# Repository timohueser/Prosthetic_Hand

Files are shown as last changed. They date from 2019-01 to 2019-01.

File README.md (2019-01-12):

# Prosthetic_Hand_V1
## Overview
The aim of this project is to design a 3D printable hand prosthesis. The hand uses 6 cheap geared DC motors that are readily available from Ebay and other places for it's 6 degrees of freedom. Motor control is achieved through a custom made Motor driver PCB that also handles force measurements for each finger. All the 3D models in STEP and STL format are available in this repository, as well as the KiCad design files and schematic of the PCB. The hand is fully self contained and only requires an external power supply and a SPI control signal to be operated. A new version of the prosthetic hand based on this design can be found here: https://github.com/timohueser/Prosthetic_Hand_V2.
<p align="center">
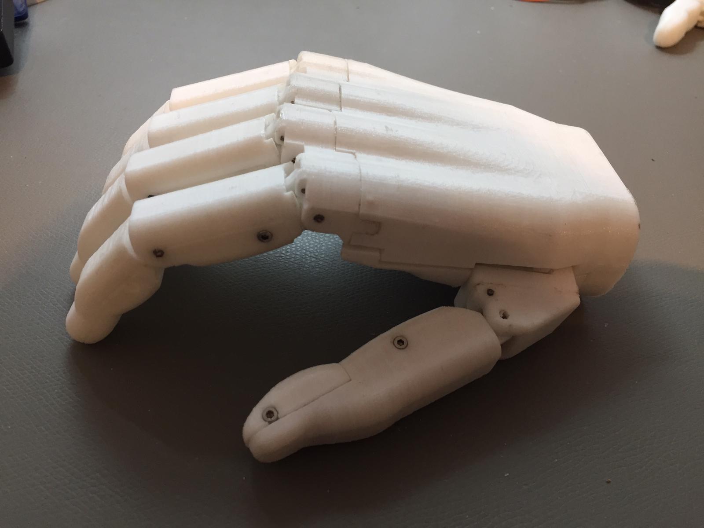
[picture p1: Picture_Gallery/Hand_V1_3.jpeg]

</p>

## Technical Details
### Fingers
The fingers are fully 3D printable and have 2 joints that move proportional to each other. It was decided to use rigid parts to drive the fingers instead of a string based system. This increases reliability and overall robustness but gives up some of the compliance that a string based system allows. The finger gets driven by a geared DC motor with a lead screw attached to its ouput shaft. A lead screw mechanism has the advantage of not being backdrivable, so the motor does not need to supply the holding torque for the fingers and only needs to be active during movement. With the motor gear ratio choosen the hand achieves reasonable movement speeds while still being able to apply ample force for tasks like picking up everyday objects. Unfortunately the way the lead screw mechanism is implemented in this version of the hand is not very durable, this is mainly due to the low quality of the lead screw and nut and the assymetric way the force gets applied to the lead screw with the current design. Version 2 of the prostehic hand mostly solves this reliability problem. Version 2 also replaces the cheap geared motors used in this version with high quality Maxon Dc motors that can produce significantly more power because of their higher efficiency. Also overall reliability of motor windings and the gearbox are obvious drawbacks of using the cheap motors compared to high quality ones. 
<p align="center">
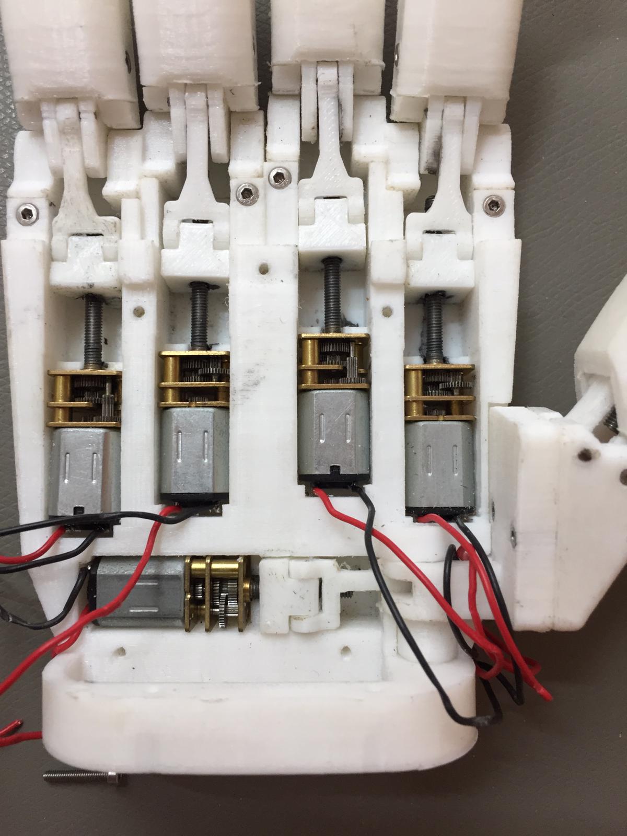
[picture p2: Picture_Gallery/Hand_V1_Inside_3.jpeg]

</p>

### Thumb
Similar to the other fingers the thumb uses a lead screw machanism to be positioned. In contrast to the other fingers the thumb has two degrees of freedom controlled by two seperate motors. One motor is placed inside the thumb itself and is responsible for flexion and extension of the thumb while the other sits inside the palm of the hand and controls abduction and adduction. This allows a variety of disserent gripping patterns, that the hand can switch bewtween quickly and without needing to be manually adjusted with the other hand. Having one of the motors inside the thumb is necessary to fit the realtively big motors choosen for this project inside the hand, but leads to a less than optimal weight distribution.
Furthermore the exact geometry, like for example the axis of rotation for abduction, still requires a lot of finetuning since the current geometry causes very unnatural positioning of the thumb for certain gripping patterns. Adding compliance to the abduction/adduction joint is a aim for version two, that is expected to greatly improve the capability of the hand to addapt do different objects.

### Motor Driver PCB
The motor driver PCB is based on the L293D Quad Half-H Driver to power the 6 DC motors. It needs to be supplied by a 9-12V motor power supply and a 3-5V supply for the logic and current sense circuitry. The motor supply should be able to handle at least 2 Amps of peak current draw. The motor driver ICs are controlled by a simple 74HC595 shift register, this enables very simple control over the hand over a standard SPI protocoll. Unfortunately there is no encoder readout for the motors for reasons of space constraint. This limits the precision the fingers can be positioned at significantly. 
In addition to motor drive capabilities the circuit also has 6 current sensors, consisting of a current sense resistor and a differential amplifier for each motor to monitor the strain on the motors. This can either be used as crude force feedback to the user of the hand or to limit the torque the hand can apply and stop motors from stalling as soon as the grip is closed. It is also useful as a homing feature since as mentioned previously there is no direct position readout for the fingers. 
Despite adding this position readout using motor drivers with better efficiency is is one of the major improvements that need to be made for the motor driver PCB used in version 2 of the prosthetic hand. The L293D drivers are very inneficient compared to more modern motor driver ICs and produce a lot of excess heat that builds up quickly in the tight and isolated environment the PCB is installed in. In addition many modern motor driver ICs have features like thermal cutoffs and motor current monitoring already built in, allowing for a much more compact PCB design. 
<p align="center">
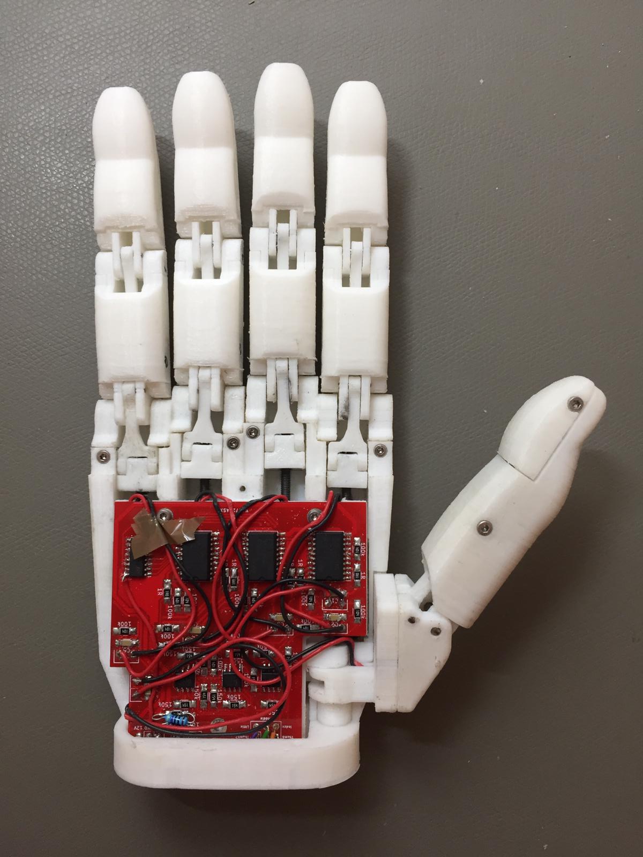
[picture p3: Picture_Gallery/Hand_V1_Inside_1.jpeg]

</p>

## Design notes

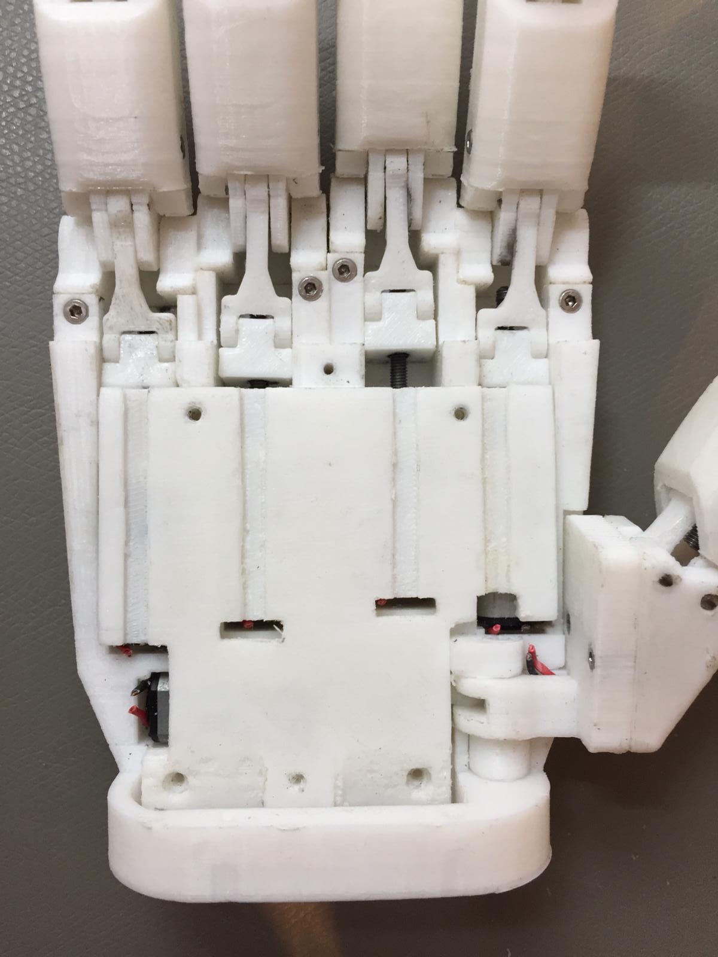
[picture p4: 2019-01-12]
Picture_Gallery/Hand_V1_Inside_2.jpeg

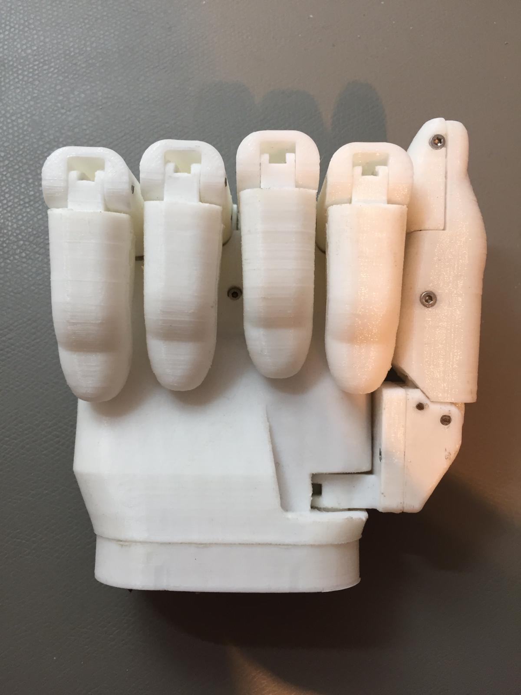
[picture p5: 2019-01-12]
Picture_Gallery/Hand_V1_2.jpeg

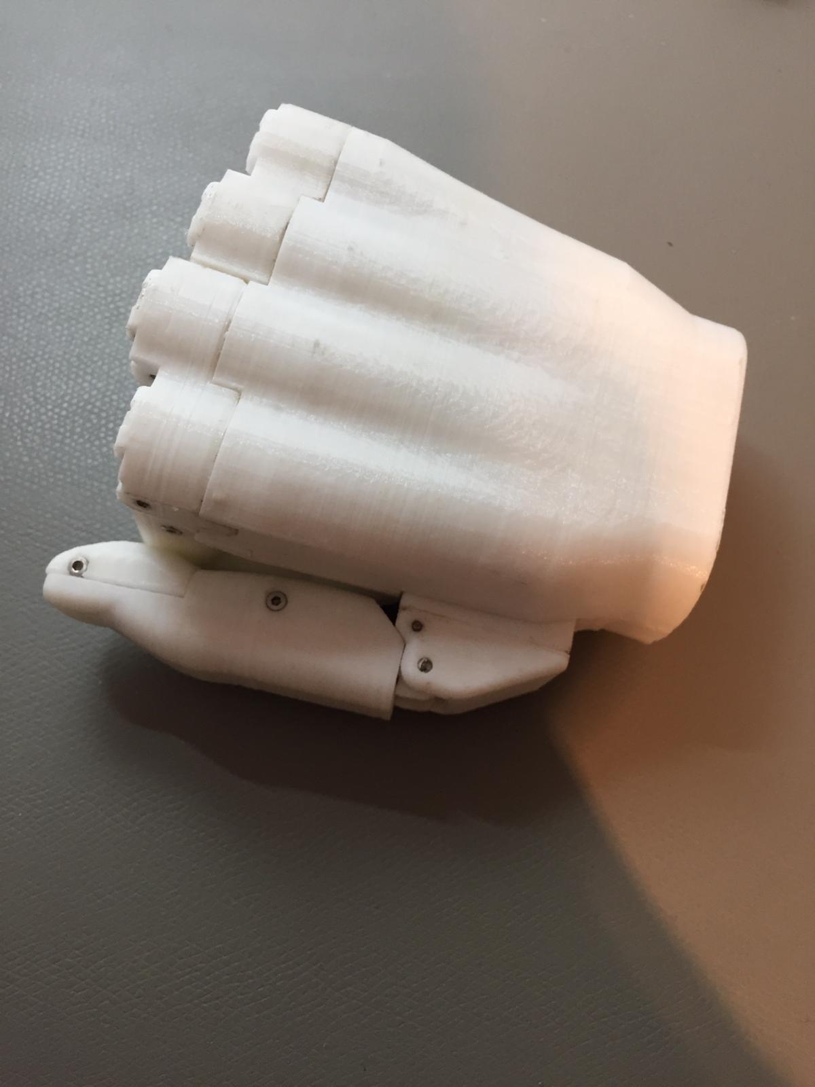
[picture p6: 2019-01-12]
Picture_Gallery/Hand_V1_4.jpeg

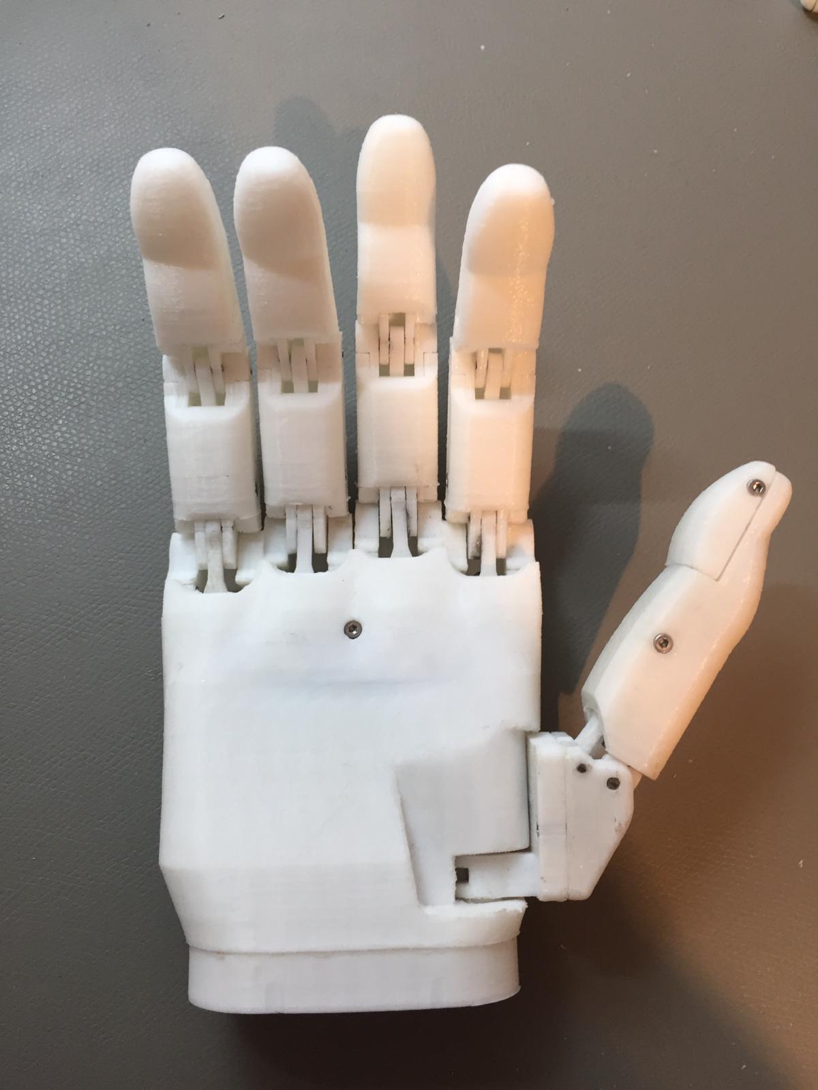
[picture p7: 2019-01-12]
Picture_Gallery/Hand_V1_1.jpeg

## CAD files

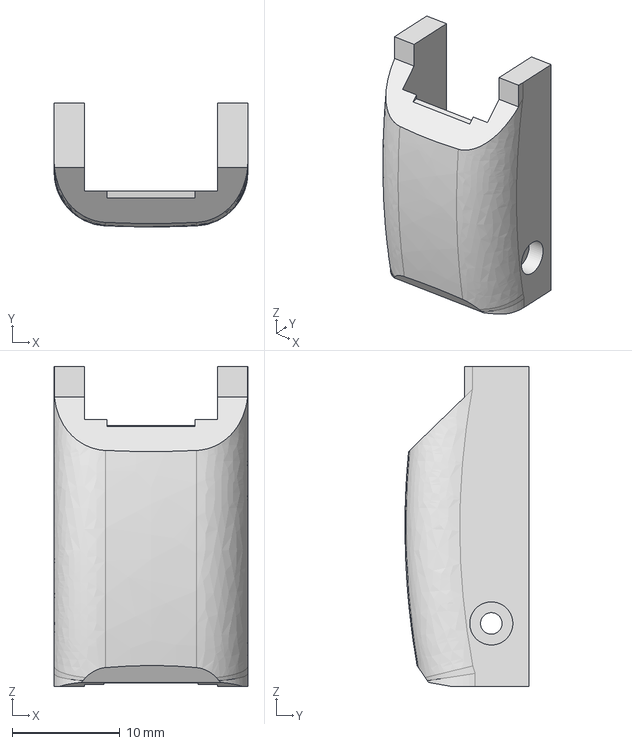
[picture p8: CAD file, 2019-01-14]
3D_Files/Finger/Lower_Part/Front.step
18.0 x 11.5 x 29.7 mm

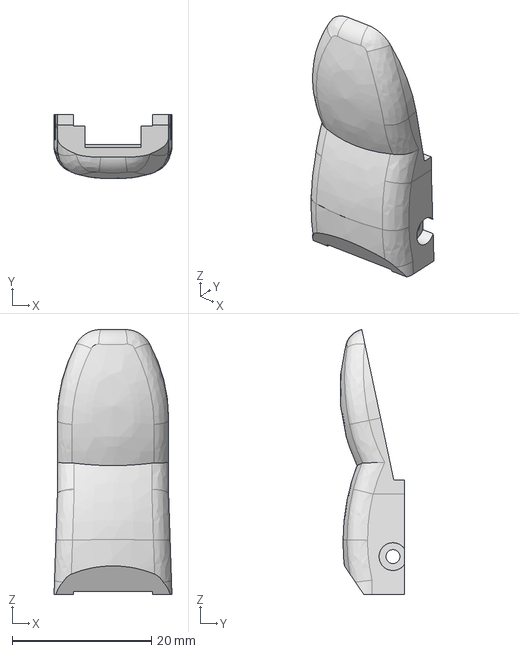
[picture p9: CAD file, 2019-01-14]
3D_Files/Finger/Upper_Part/Front.step
17.0 x 9.19 x 38.1 mm

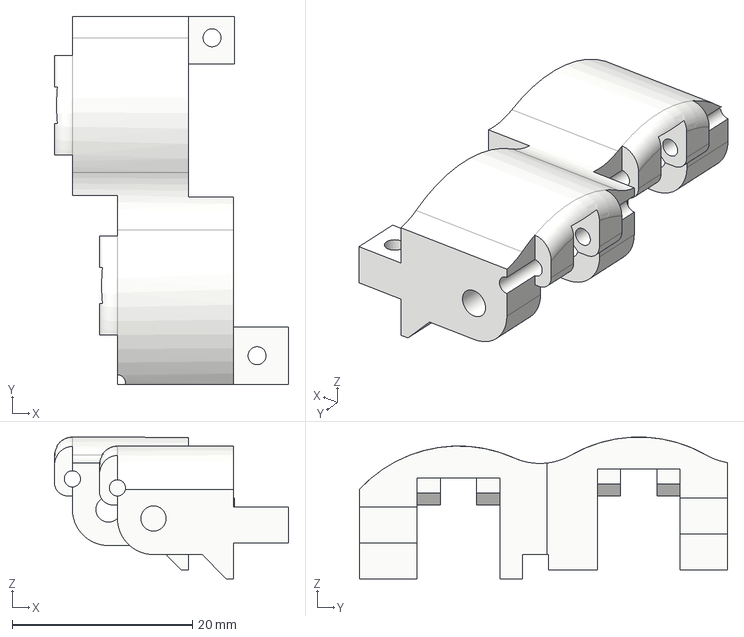
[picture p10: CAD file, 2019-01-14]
3D_Files/Palm/Finger_Mounts2.step
26.0 x 40.9 x 15.7 mm

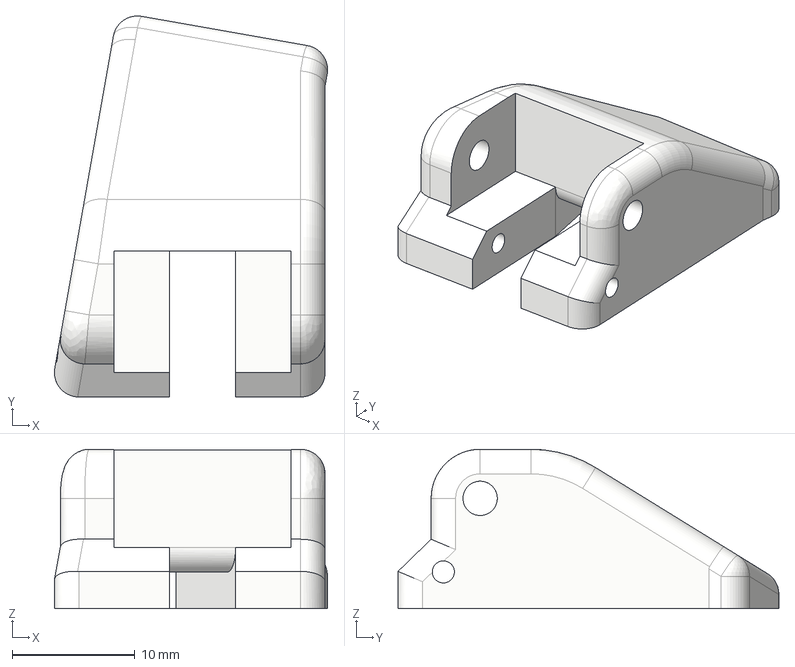
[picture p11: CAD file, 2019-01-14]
3D_Files/Thumb/Lower_Part/Base.step
22.3 x 31.1 x 13.0 mm

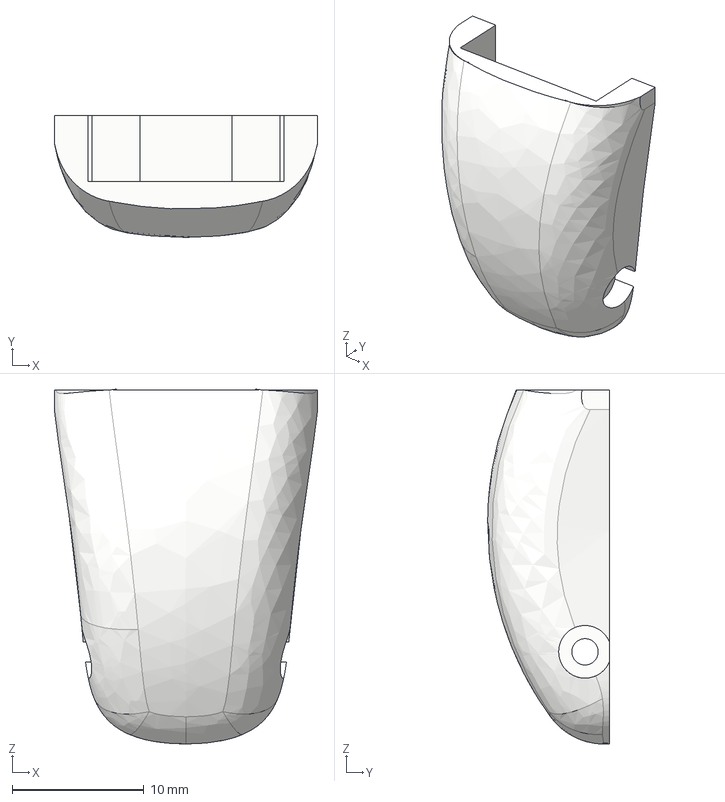
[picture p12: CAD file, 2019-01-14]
3D_Files/Thumb/Upper_Part/Tip.step
20.0 x 9.25 x 27.0 mm

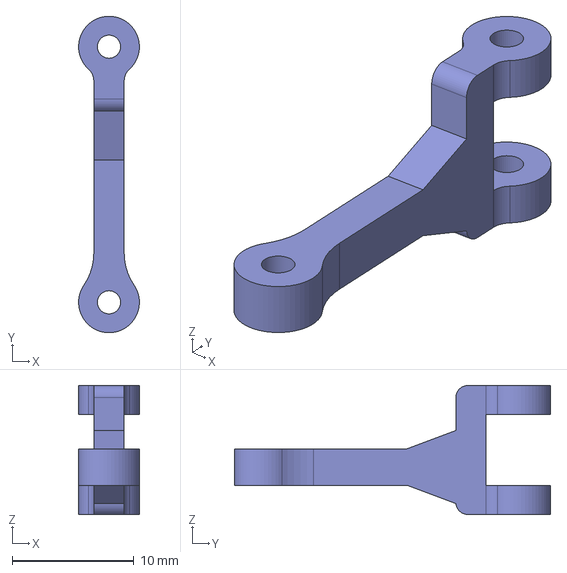
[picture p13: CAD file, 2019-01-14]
3D_Files/Finger/Lower_Part/Link.step
5.00 x 26.0 x 10.6 mm

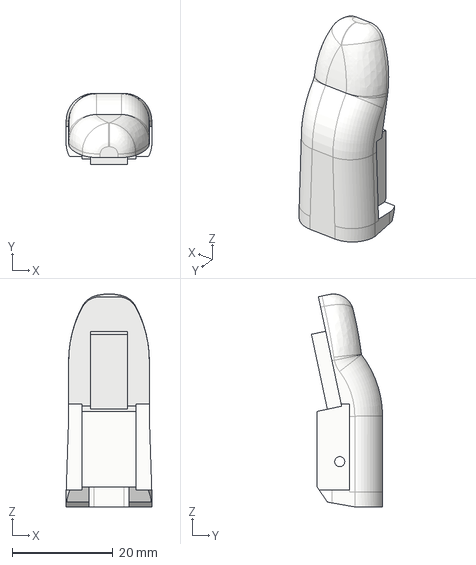
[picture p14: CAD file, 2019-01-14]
3D_Files/Finger/Upper_Part/Back.step
17.0 x 14.1 x 42.3 mm

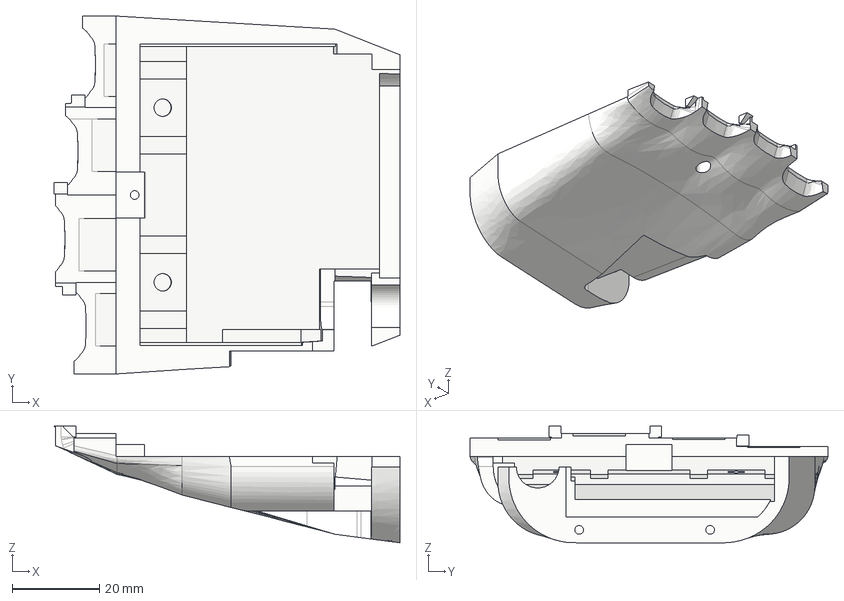
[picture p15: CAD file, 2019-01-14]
3D_Files/Palm/Palm.step
79.3 x 82.0 x 26.7 mm

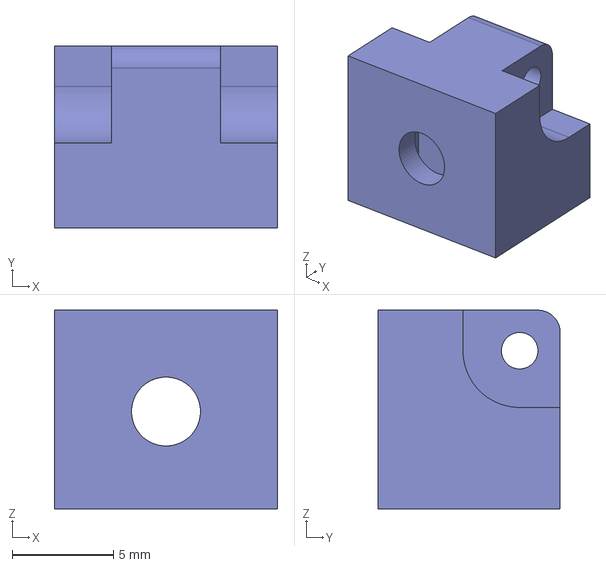
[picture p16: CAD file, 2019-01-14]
3D_Files/Thumb/Lower_Part/Slider.step
11.0 x 9.00 x 9.80 mm

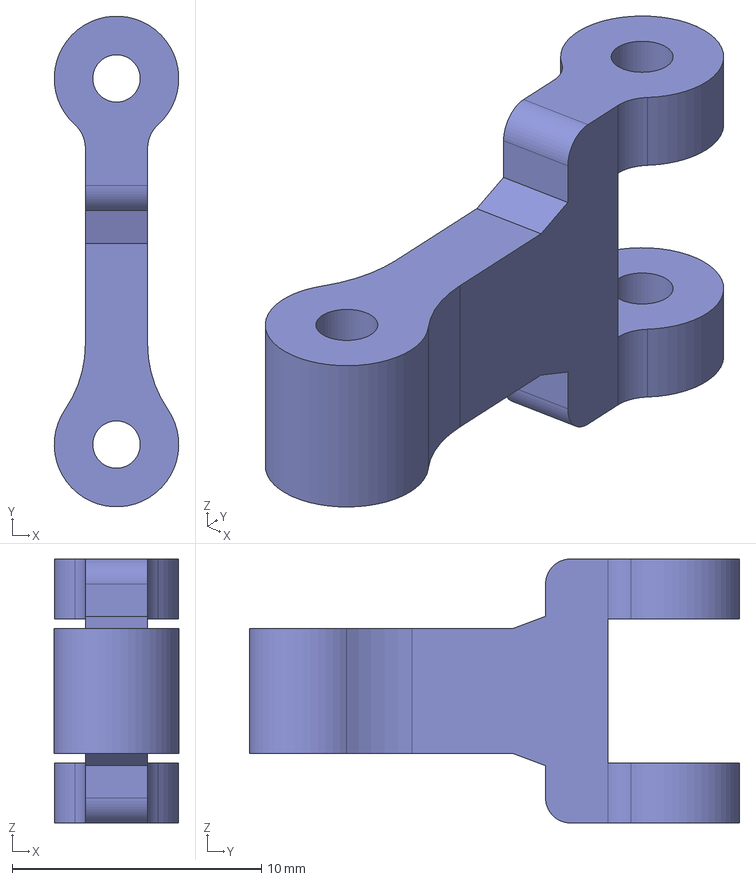
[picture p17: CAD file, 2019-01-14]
3D_Files/Thumb/Upper_Part/Link.step
5.00 x 19.7 x 10.6 mm

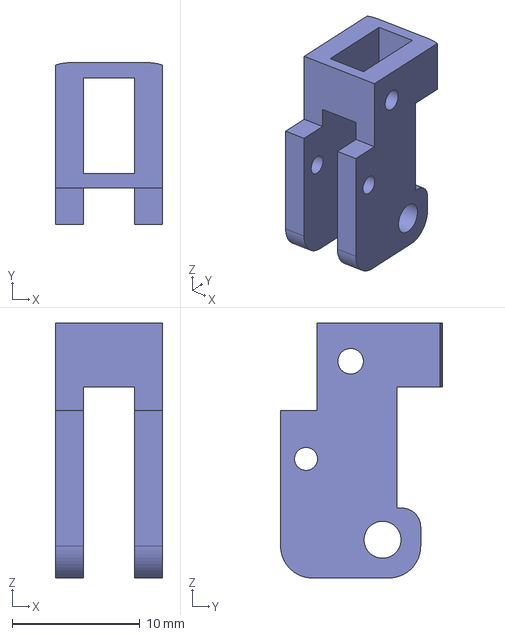
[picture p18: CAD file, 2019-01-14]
3D_Files/Finger/Lower_Part/Base.step
8.40 x 12.7 x 20.0 mm

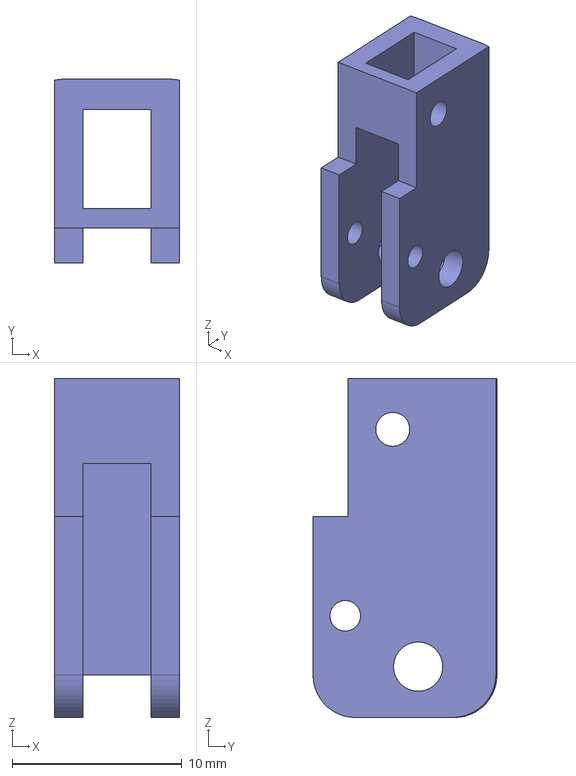
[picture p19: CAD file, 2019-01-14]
3D_Files/Finger/Upper_Part/Base.step
7.40 x 10.9 x 20.0 mm

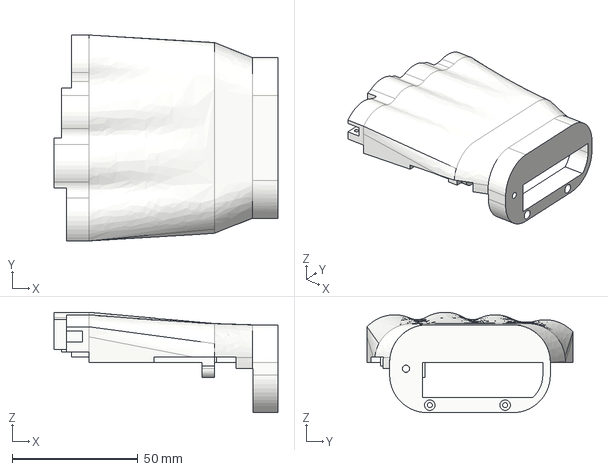
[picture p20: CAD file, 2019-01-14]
3D_Files/Palm/Base.step
89.2 x 82.0 x 40.0 mm

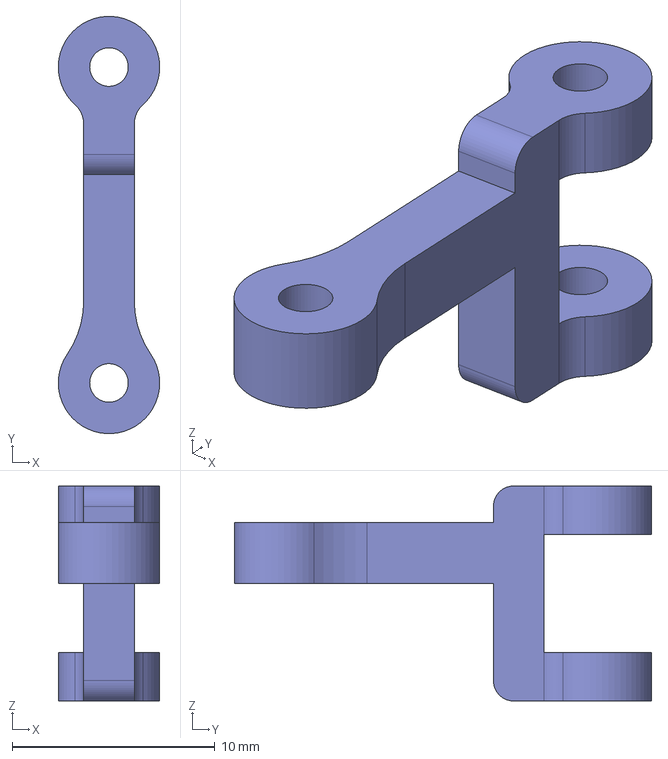
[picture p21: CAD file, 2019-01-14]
3D_Files/Thumb/Lower_Part/Link.step
5.00 x 20.6 x 10.6 mm

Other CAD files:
3D_Files/Thumb/Upper_Part/Slider.step
3D_Files/Finger/Lower_Part/Back.step
3D_Files/Finger/Upper_Part/Link.step
3D_Files/Palm/Board_Mount.step
3D_Files/Finger/Lower_Part/Back.stl
3D_Files/Finger/Lower_Part/Base.stl
3D_Files/Finger/Lower_Part/Front.stl
3D_Files/Finger/Lower_Part/Link.stl
3D_Files/Finger/Lower_Part/Slider.step
3D_Files/Finger/Lower_Part/Slider.stl
3D_Files/Finger/Upper_Part/Back.stl
3D_Files/Finger/Upper_Part/Base.stl
3D_Files/Finger/Upper_Part/Front.stl
3D_Files/Finger/Upper_Part/Link.stl
3D_Files/Palm/Base.stl
3D_Files/Palm/Board_Mount.stl
3D_Files/Palm/Finger_Mounts1.step
3D_Files/Palm/Finger_Mounts1.stl
3D_Files/Palm/Finger_Mounts2.stl
3D_Files/Palm/Palm.stl
3D_Files/Thumb/Lower_Part/Base.stl
3D_Files/Thumb/Lower_Part/Joint.step
3D_Files/Thumb/Lower_Part/Joint.stl
3D_Files/Thumb/Lower_Part/Link.stl
3D_Files/Thumb/Lower_Part/Slider.stl
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

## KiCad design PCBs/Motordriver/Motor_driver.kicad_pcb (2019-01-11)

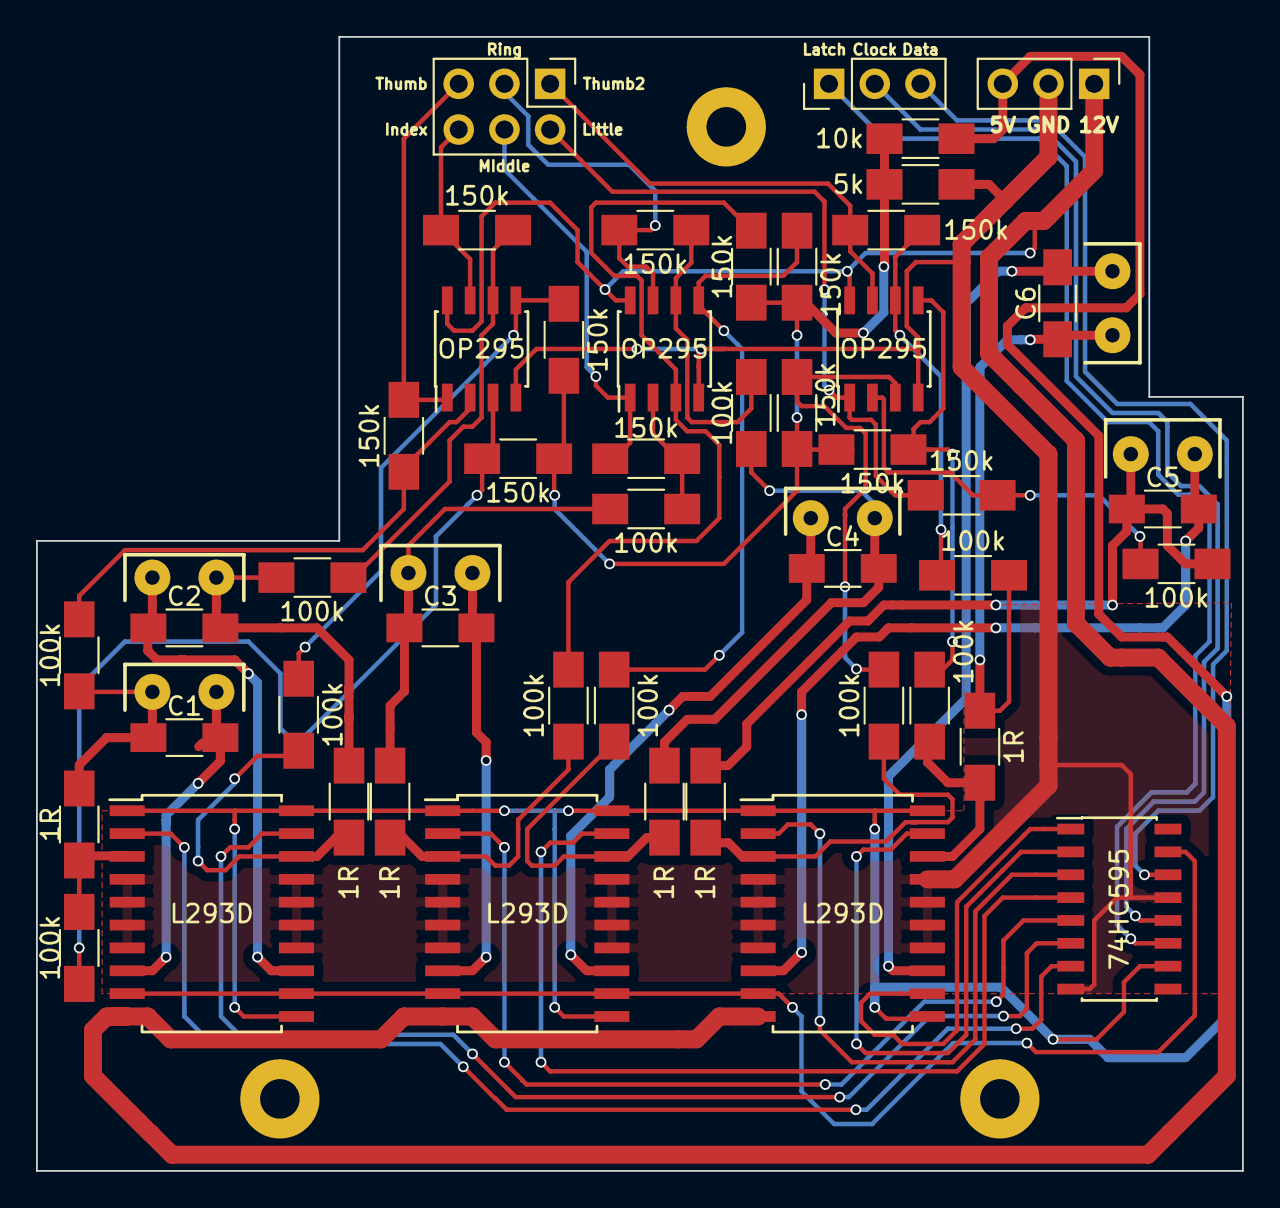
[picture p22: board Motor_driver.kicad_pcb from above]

Board: 2 copper layers, 67.0 x 63.0 mm, 60 parts (0 on the bottom side), 51 nets.

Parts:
74HC595: 74HC595; SOIC-16_3.9x9.9mm_Pitch1.27mm
C1, C2, C3, C4, C5, C6: C; C_1206_HandSoldering
L293D, L293D#2, L293D#3: L293D; SOIC-20W_7.5x12.8mm_Pitch1.27mm
OP295, OP295#2, OP295#3: TL072; SOIC-8_3.9x4.9mm_Pitch1.27mm
P1, P2, P3, P4, P5, P7, P8, P9, P10, P18, P19: CONN_01X01; SolderWirePad_single_0-8mmDrill
P11, P12: CONN_01X03; Pin_Header_Straight_1x03_Pitch2.54mm
P13: CONN_01X06; Pin_Header_Straight_2x03_Pitch2.54mm
R1, R2, R3, R4, R5, R26: 1R; R_1206_HandSoldering
R6, R7, R12, R13, R14, R17, R18, R19, R24, R25, R27, R30: 150k; R_1206_HandSoldering
R8, R9, R10, R11, R15, R16, R20, R21, R22, R23, R28, R29: 100k; R_1206_HandSoldering
R31: 5k; R_1206_HandSoldering
R32: 10k; R_1206_HandSoldering
wP6: CONN_01X01; SolderWirePad_single_0-8mmDrill

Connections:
+2V5: R12.1, R13.1, R17.1, R24.1, R25.1, R30.1, R31.1, R32.2
+5V: 74HC595.10, L293D.1, L293D.11, L293D.20, L293D#2.1, L293D#2.11, L293D#2.20, L293D#3.1, L293D#3.11, L293D#3.20, P11.3, R32.1
+12V: L293D.10, L293D#2.10, L293D#3.10, OP295.8, OP295#2.8, OP295#3.8, P11.1
Clock: 74HC595.12, P12.2
Common: 74HC595.15, L293D.9, L293D.12, L293D#2.9, L293D#2.12, L293D#3.9
Data: 74HC595.14, P12.3
GND: 74HC595.8, 74HC595.13, L293D.4, L293D.5, L293D.6, L293D.7, L293D.14, L293D.15, L293D.16, L293D.17, L293D#2.4, L293D#2.5, L293D#2.6, L293D#2.7, L293D#2.14, L293D#2.15, L293D#2.16, L293D#2.17, L293D#3.4, L293D#3.5, L293D#3.6, L293D#3.7, L293D#3.14, L293D#3.15, L293D#3.16, L293D#3.17, OP295.4, OP295#2.4, OP295#3.4, P11.2, R31.2
Index: 74HC595.6, L293D.19
IndexSen1: L293D.18, R2.2, R9.2
IndexSen2: C2.1, P1.1, R2.1, R11.2
Latch: 74HC595.11, P12.1
Little: 74HC595.3, L293D#3.2
LittleSen1: L293D#3.3, R5.2, R21.2
LittleSen2: C5.1, P4.1, R5.1, R23.2
Middle: 74HC595.5, L293D#2.2
MiddleSen1: L293D#2.3, R3.2, R15.2
MiddleSen2: C3.1, P2.1, R3.1, R16.2
unnamed: C1.2, L293D.8, wP6.1
unnamed: C2.2, L293D.13, P7.1
unnamed: C3.2, L293D#2.8, P8.1
unnamed: C4.2, L293D#2.13, P9.1
unnamed: C5.2, L293D#3.8, P10.1
unnamed: C6.2, L293D#3.13, P19.1
unnamed: OP295#3.7, P13.1, R27.1
unnamed: OP295#3.1, P13.2, R19.1
unnamed: OP295#2.7, P13.3, R18.1
unnamed: OP295#2.1, P13.4, R14.1
unnamed: OP295.1, P13.5, R6.1
unnamed: OP295.7, P13.6, R7.1
unnamed: OP295.2, R6.2, R10.1
unnamed: OP295.6, R7.2, R11.1
unnamed: OP295.3, R8.1, R12.2
unnamed: OP295.5, R9.1, R13.2
unnamed: OP295#2.2, R14.2, R16.1
unnamed: OP295#2.3, R15.1, R17.2
unnamed: OP295#2.6, R18.2, R22.1
unnamed: OP295#3.2, R19.2, R23.1
unnamed: OP295#2.5, R20.1, R24.2
unnamed: OP295#3.3, R21.1, R25.2
unnamed: OP295#3.6, R27.2, R29.1
unnamed: OP295#3.5, R28.1, R30.2
Ring: 74HC595.4, L293D#2.19
RingSen1: L293D#2.18, R4.2, R20.2
RingSen2: C4.1, P3.1, R4.1, R22.2
Thumb1: 74HC595.7, L293D.2
Thumb2Sen1: L293D#3.18, R26.2, R28.2
Thumb2Sen2: C6.1, P18.1, R26.1, R29.2
Thumb2_a: 74HC595.2, L293D#3.19
Thumb2_b: 74HC595.1, L293D#3.12
ThumbSen1: L293D.3, R1.2, R8.2
ThumbSen2: C1.1, P5.1, R1.1, R10.2
